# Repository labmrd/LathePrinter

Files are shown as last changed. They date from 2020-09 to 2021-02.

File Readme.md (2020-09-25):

# Lathe 3D Printer

This documentation package includes all of the instructions, materials, models, and code required to construct your own version of the University of Minnesota Medical Robotics and Devices Lab Lathe 3D printer developed by John Huss. This open source design allows a user to create 3D printed balloon catheter segments, for use in constructing robots or other cylindrical 3D printed objects.

## Links to the lab:
- [Research lab](http://dept.me.umn.edu/labs/mrd/)
- [Project motivation](http://dept.me.umn.edu/labs/mrd/Soft_Robots.shtml)

Included in this design are the files needed to recreate the complete fused filament fabrication test bench version of this printer plus the preliminary models and instructions for a fiber reinforced photopolymer extrusion version.

## System features:
The printer utilizes a horizontal lathe-style arrangement of axes to print high aspect ratio cylindrical objects more efficiently and accurately than other methods. This is achieved by using a rotating mandrel as a removable deposition surface. This mandrel can be removed after the printing is finished, leaving a hollow, highly accurate cylinder. Additionally, to ensure straightness of the mandrel two counter-rotating motors (one at each end of the long axis) are used to eliminate any torsional strain in the mandrel. The collets at both ends in which the mandrel is held can be moved along the axis to pre-strain the deposition surface to eliminate gravitational sag and any bends in the mandrel.

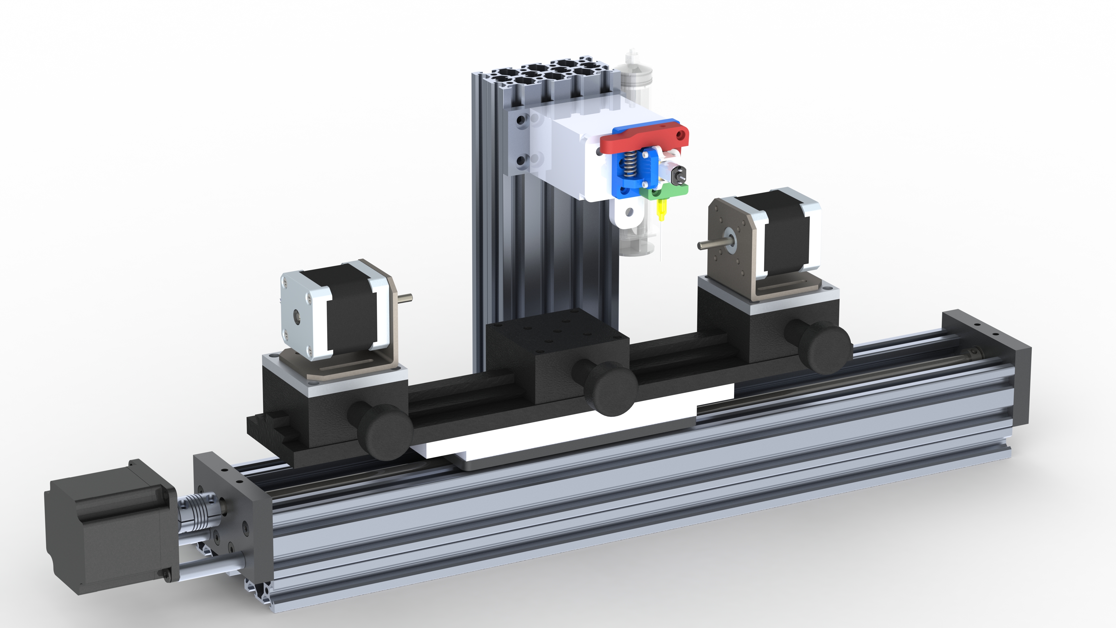
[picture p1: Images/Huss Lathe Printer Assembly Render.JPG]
Solidworks model of the printer


## Coordinates and axis definitions:
This printer operates in a polar coordinate system (R, theta, Z). Z, along the length of the cylinder, is operated by an [OpenBuilds linear actuator](https://openbuildspartstore.com/c-beam-linear-actuator-bundle) and forms the structural base of the printer. The rotational axis, theta (Y axis in the firmware), is operated by two counter-rotating stepper motors mounted to an optics positioning stage on the sliding potion of the Z axis linear carriage. The optics stage allows for fine tuning of the distance between the two theta axis motors to accommodate different length mandrels. Additionally, a third optics stage between motor mounts provides a convenient location to mount any measuring equipment or dial indicators. The final axis, R (X in firmware), is vertical and is currently entirely manual. Motion of the R axis is achieved by adjusting the head mount linear stage attaching the nozzle to the head support column. One final minor adjustment axis is available to move the print head forwards and backwards for calibration by adjusting the second dial on the head mount linear stage. This minor axis allows the user to position the head precisely over the mandrel.

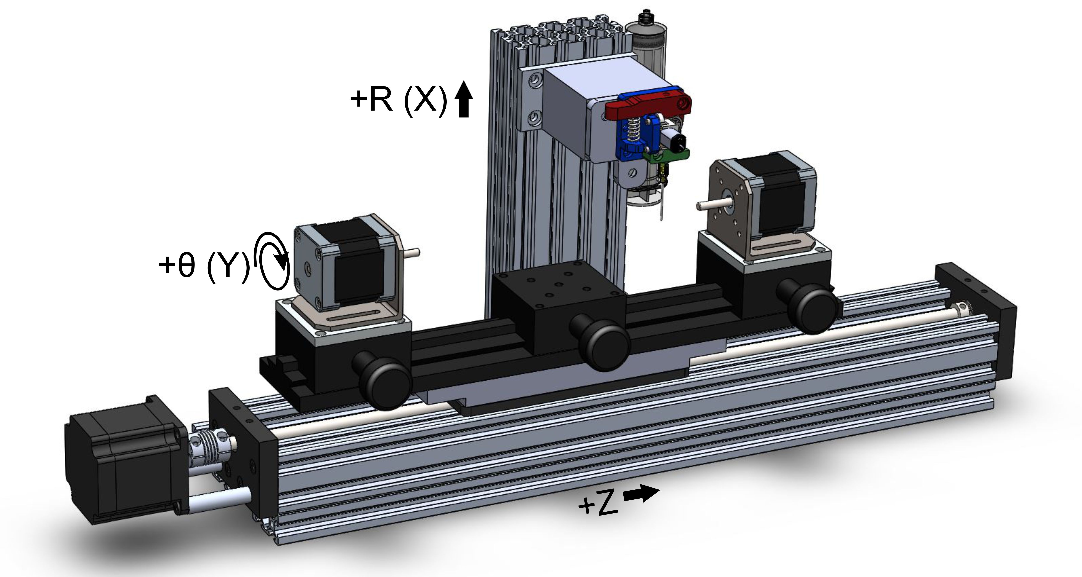
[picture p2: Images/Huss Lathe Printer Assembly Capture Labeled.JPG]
Axes


## Software and slicing:
This printer accepts standard 3D printer G-code, but with some restrictions. The system will fail to print if the requested nozzle position is within R=1mm (representing the minimum R position because of the mandrel). Traditional slicers prepare 3D printer G-code by turning the CAD model into a series of 2D layers from -Z to +Z, which is not how this printer is constructed. This system requires G-code with layers ordered from -R to +R. If the user only needs single layer thickness models, they should use a commonly available feature of slicers often called "vase mode" to create single nozzle width walls. In this case, the walls are layers. To achieve thicker cylinders there are a few options. 
1. Run the print again with the manual R axis set slightly higher and adjust the extrusion rate modifier accordingly in the control console. 
2. If the user automates the R axis, slice a second cylinder model with a slightly wider radius and print that onto the first model. 
3. Generate or modify G-code using a different method such as a custom MATLAB or Python script, or process existing G-code files into one continuous file.
Slicing models for this printer is the biggest area of needed improvement and will change depending on the user's desired use case. The above methods are suggested starting points for researchers to build from.

## Firmware:
This printer uses a Duet2 Ethernet controller board and an older version of dc42's Duet Firmware package [RepRapFirmware](https://github.com/Duet3D/RepRapFirmware) has been configured for this system. The configuration file and homing files (with comments) are included in this documentation package. The specific G codes supported in this firmware package are [documented here](https://duet3d.dozuki.com/Wiki/Gcode).

## Electronics and Wiring:
The wiring for this project is standard for a 3D printer using stepper motors with a few exceptions. Only one axis requires an end-stop, Z, because R is manual, and theta is continuous. This endstop is not pictured in the CAD files but can be seen mounted to the linear actuator on the left side of the carriage in the photographs. To achieve counter-rotating mandrel motors both motors are plugged into the Z-axis motor ports on the Duet board. Duet supports two Z axis motors in parallel at the hardware level for large print beds. There are two ports connected to the same motor driver chip. To force one motor to spin in reverse of the other, reverse the pin-out of one pair of wires on the stepper motor. This will cause it to rotate the other way compared to the first motor. It does not matter which pair you swap as long as they are from the same winding. You can check for continuity between each pair of wires to know which go together before swapping. The Z axis motor ports on the board are configured in firmware to act as the rotational axis of the polar printer instead of as the Z axis.

### Wiring diagram:
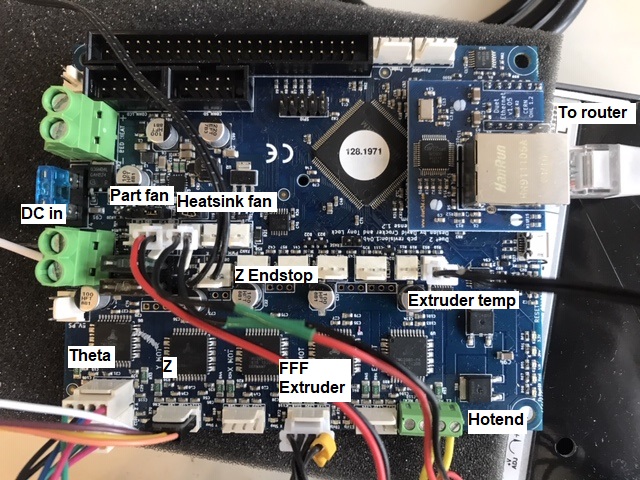
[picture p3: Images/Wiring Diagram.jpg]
Electronics wiring diagram


### Dual theta stepper motor wire swap
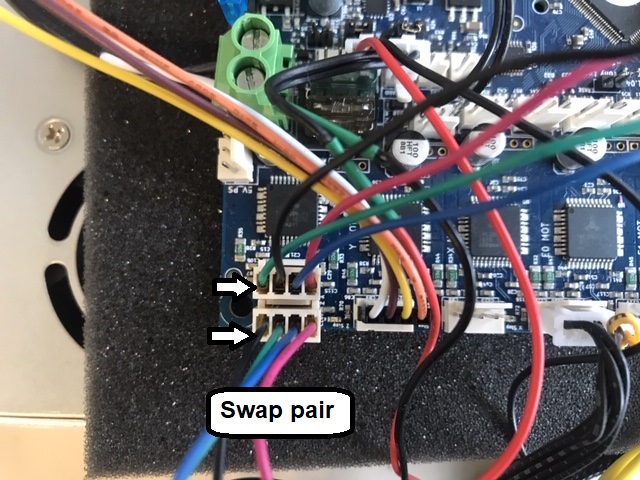
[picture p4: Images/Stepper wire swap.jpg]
Stepper motor wire swap


## Hardware design:
Many components of this printer are available for purchase or can be made using other common 3D printers and machining techniques. The main structure of this system is created from aluminum extrusions, assembled using T-slot nuts, bolts, and brackets. The full Bill of Materials in included for a more detailed view of all necessary components. Most of the mounting hardware is not shown in the CAD files, so use the pictures to see how I assembled it. Feel free to make changes. See the Images folder for detailed photos of the assembly.

## Extrusion systems:
Two extrusion systems currently exist for this printer, a traditional fused filament fabrication extruder, and an experimental fiber reinforced photopolymer co-extruder. The FFF extruder is a standard Creality CR-10 extruder and hotend assembly adapted to fit onto the head column. The experimental co-extrusion fiber/photopolymer system is based on a CR-10 extruder, but highly modified with experimental 3D printed components. Once complete this second system will allow a user to create highly elastic air-tight cylinders with built-in strain-limiting fibers. These fibers can be used to modify the behavior of the cylinders when they are inflated, which is an ongoing research topic within the MRD Lab.

## Example FFF print:
A sample part is included along with instructions in video form on how to get started, from printer assembly to firmware installation, slicing and printing. This sample part is a simple one-layer thick cylindrical model.

### Getting connected if your network uses DHCP
In a university research lab setting I found it difficult to configure the printer to always use a static IP address. There are three main options, with some clearly better than others. The first and best option is to let your network manager assign this device a static IP using the MAC address listed in the config.g file (you can change this if there is a conflict). If that isn't an option you can set up your own small offline network and configure your router to assign the printer a static IP. This is how the printer is currently configured. Alternatively, you can connect directly to a computer but I found it simpler to use a router. Finally, and not recommended, you can let the printer use DHCP on the university network and interrogate the printer over USB to discover its assigned IP address. To do this connect via the USB cable and use a slicing program (I used Matter Control) that has a Terminal window. Connect using the terminal and send M552 to find out the current network settings.

### Notes on choosing your own hardware and electronics:
Many of the components for this printer were chosen primarily due to their availability in the lab already and my familiarity with them. If you want to choose different components (possibly cheaper) that is certainly an option. The full capabilities of the power supply, mainboard, and even the full accuracy of the optics components are not being used in this current form, but for a research platform it is helpful to eliminate any potential issues from incompatible or underperforming equipment. It may be possible to extract the motors, power supply, and electronics from a more inexpensive 3D printer to build this system, but I haven't tested compatibility with anything else. Possible hurdles may arise with the polar setup if a different mainboard/firmware combination doesn't support this kinematics type.

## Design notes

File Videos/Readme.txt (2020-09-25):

Unfortunately, a few of these videos are missing some content. Two of the videos were recorded Zoom meetings with a secondary camera pointed at the phyical printer. This wasn't captured properly in the recordings. Use your imagination I guess.

Videos are hosted in Google Drive, here:
https://drive.google.com/drive/folders/1oRndGqx4MNpRWvz8KzQ8WXYX7neBrAih?usp=sharing

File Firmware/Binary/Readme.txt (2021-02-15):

This is the binary to install through Duet Web Control onto your Duet board. This is the version I used, which is likely now outdated. Update as you see fit. 
As of 2/15/2021 it looks like the firmware project is located at https://github.com/Duet3D/RepRapFirmware

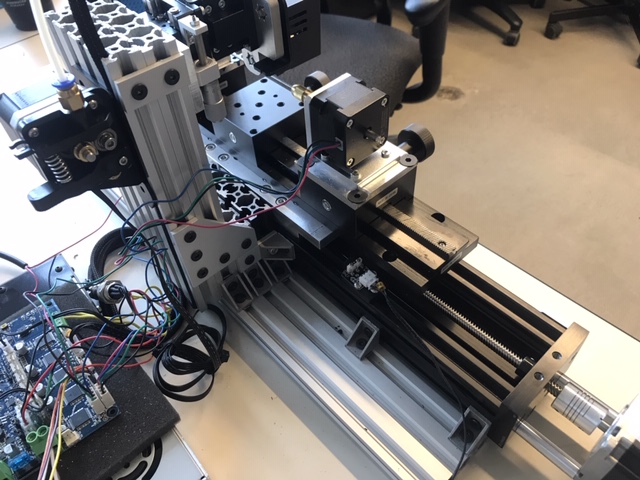
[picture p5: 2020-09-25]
Images/Left 2.jpg

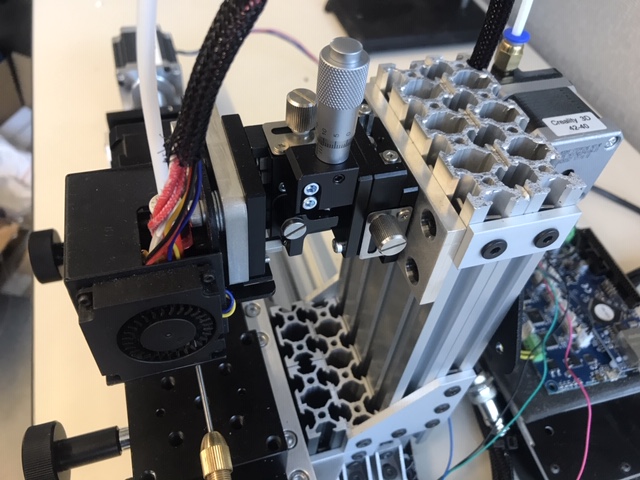
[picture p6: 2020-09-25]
Images/Right Top.jpg

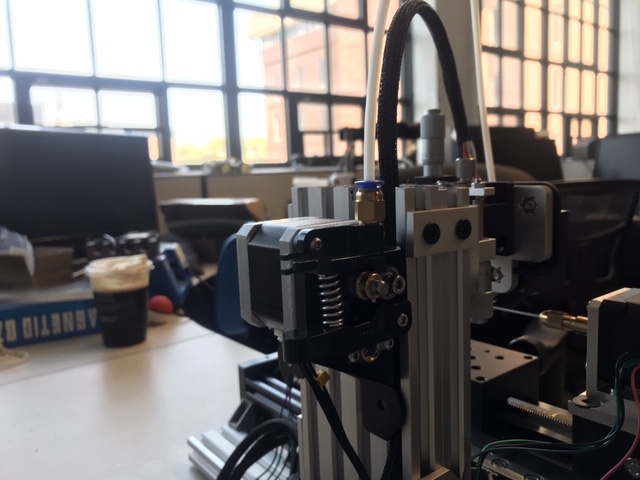
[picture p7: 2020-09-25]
Images/Extruder.jpg

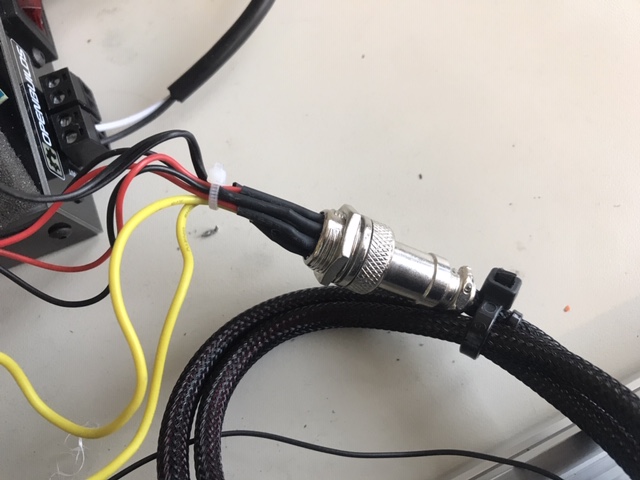
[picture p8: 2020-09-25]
Images/CR10 Wire Bundle.jpg

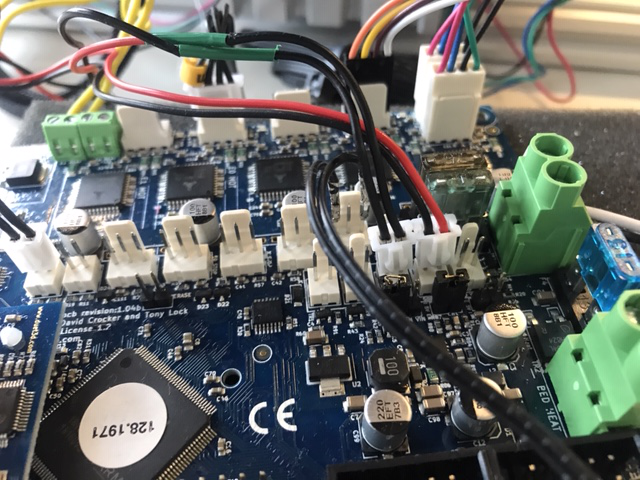
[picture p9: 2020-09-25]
Images/Board Back.jpg

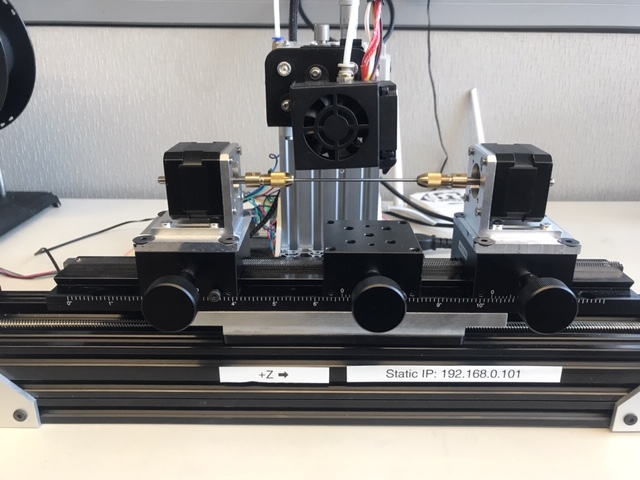
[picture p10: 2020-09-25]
Images/Front.jpg

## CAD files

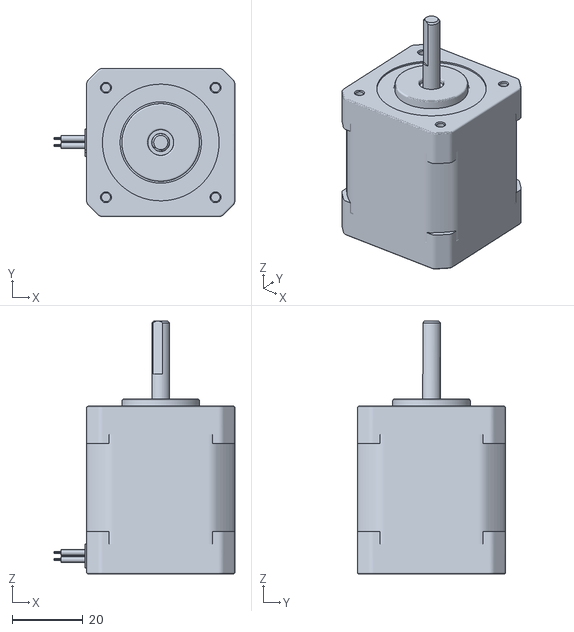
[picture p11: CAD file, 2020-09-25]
CAD/STL Assembly/LathePrinter - Z Carriage Assembly-1 NEMA17 Stepper-2.STL
51.2 x 42.0 x 71.6

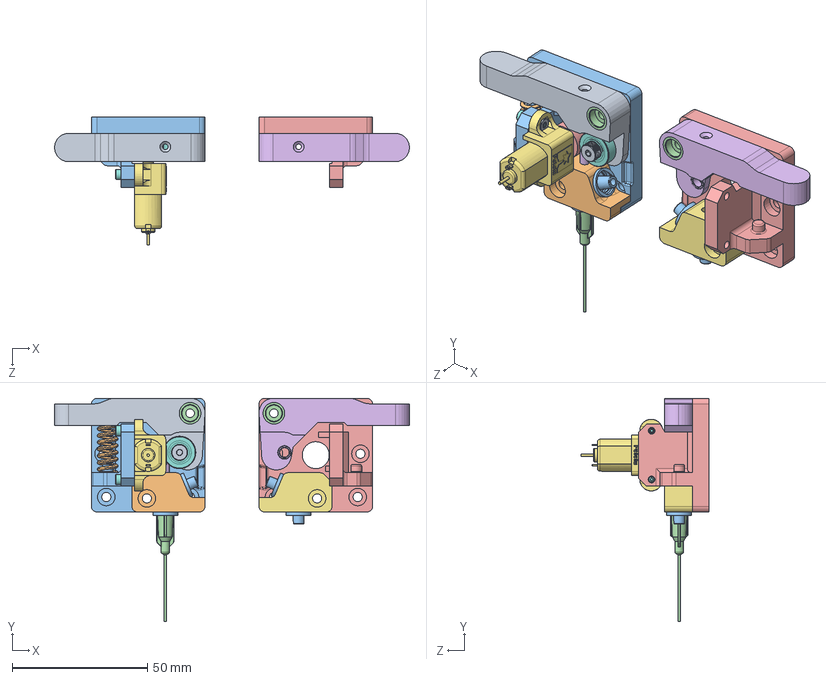
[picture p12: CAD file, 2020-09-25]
CAD/Solidworks 2019 Assembly/Experimental Extruder Dual Extruder.SLDASM
131.3 x 82.6 x 47.3 mm
ExtruderCR10 lever mirrored
ExtruderCR10 spring
Extruder custom base mirrored
ExtruderCR10 bushing x 2
SLA Printed Driver
52335K910 TUBING MADE WITH PTFE cut to size
micro-metal-gearmotor-extended-with-1086-bracket (1)
91290A015_BLACK-OXIDE CLASS 12.9 SOCKET HEAD CAP SCREW x 2
91828A111_TYPE 18-8 STAINLESS STEEL HEX NUT
SLA Printed Manifold
Luer male print with manifold x 4
Syringe Needle, With Luer
MirrorExtruder custom base
MirrorExtruderCR10 lever
MirrorPart21
7804K102_STAINLESS STEEL BALL BEARING
91273A351_SAME-SIZE THREAD 18-8 SS SHOULDER SCREW

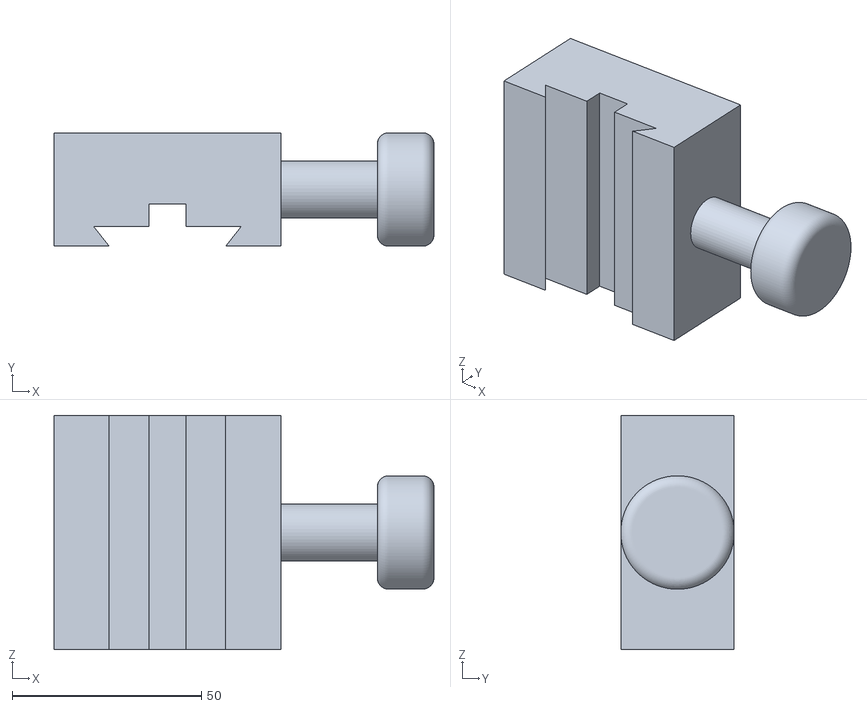
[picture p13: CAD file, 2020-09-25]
CAD/STL Assembly/LathePrinter - Z Carriage Assembly-1 Edmund Optics Knob Stage-5.STL
100.5 x 30.0 x 62.0

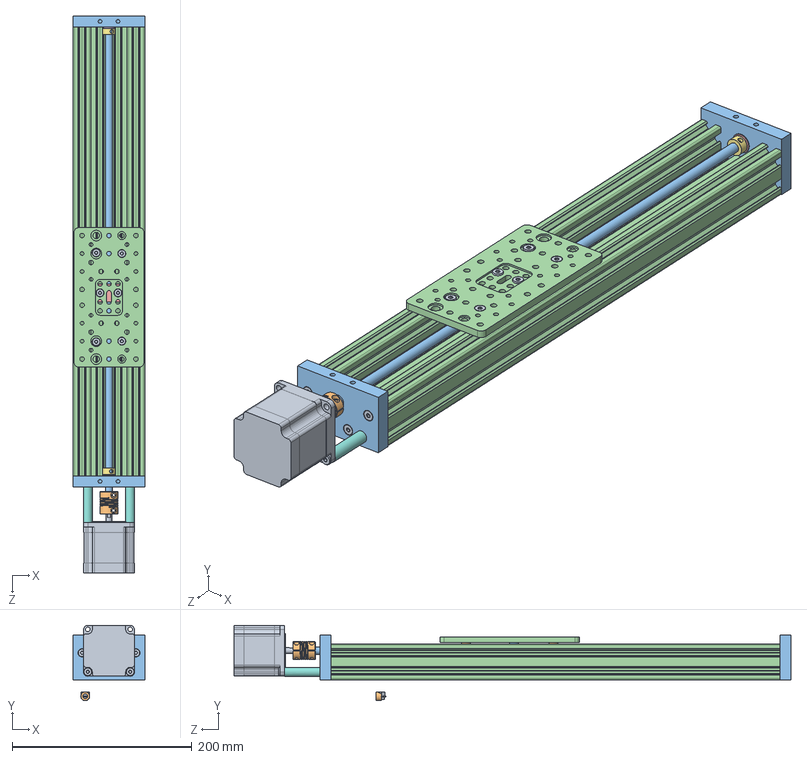
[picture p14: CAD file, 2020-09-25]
CAD/Solidworks 2019 Assembly/C-Beam Doublewide Linear Actuator 500mm.SLDASM
80.0 x 84.0 x 620.0 mm
Low Profile Screw M5 x 16
Nylon Insert Lock Nut M5 x 6
C-Beam End Mount x 2
C-Beam 40x80x500 Linear Rail
Ball Bearing 8 x 16 x 5 x 2
Shim Washer 8mm x 2
Lock Collar 8mm x 2
Aluminum Spacer 40mm x 2
Nema 23 Stepper Motor
Flexible Coupling 0.25in x 8mm
8mm leadscrew 540mm
Double CB-Gantry Plate
8mm Acme Nut Block
Xtreme Mini V Wheel x 4
Ball Bearing 5 x 10 x 4.2 x 8
Precision Shim 8 x 5 x 1 x 8
Mini Eccentric Spacer 6mm x 4
Aluminum Spacer 6mm x 4
Aluminum Spacer 3mm x 2

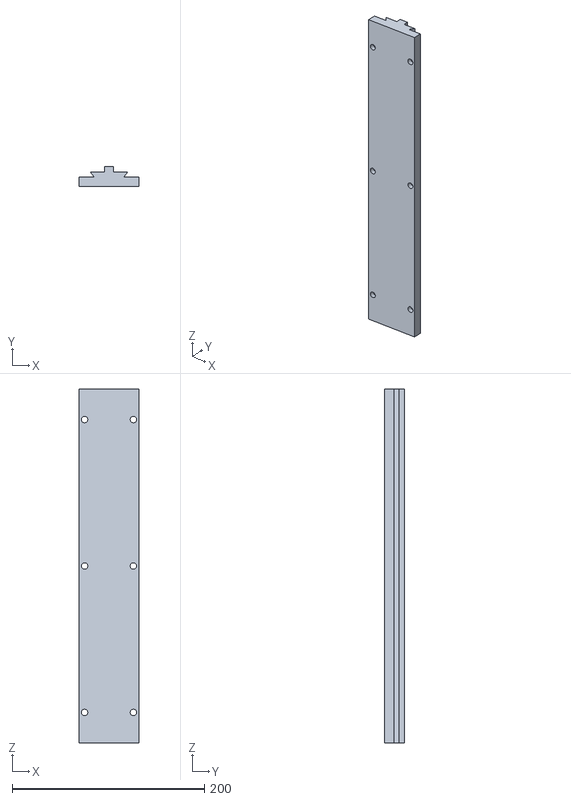
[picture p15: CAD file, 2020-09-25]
CAD/STL Assembly/LathePrinter - Z Carriage Assembly-1 Edmund Optics Linear Bearing-1.STL
62.0 x 21.1 x 368.5

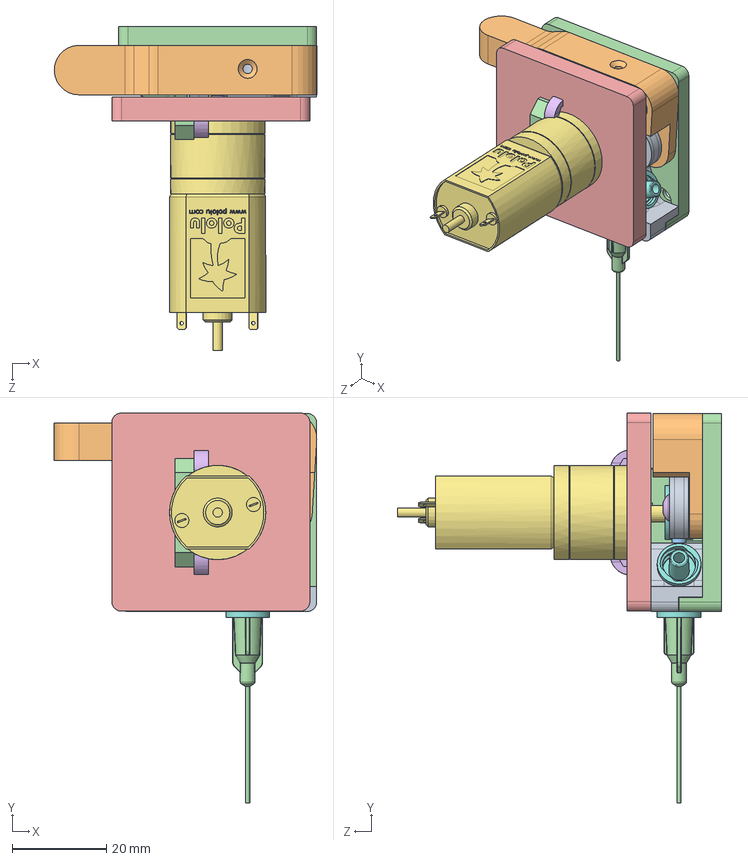
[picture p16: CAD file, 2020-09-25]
CAD/Solidworks 2019 Assembly/Extruder mini gear motor custom metal liner.SLDASM
55.7 x 82.7 x 68.7 mm
ExtruderCR10 idler
ExtruderCR10 lever
ExtruderCR10 spring
Extruder custom base
ExtruderCR10 bushing
ExtruderCR10 M3
94510A240_BRASS SCREW-TO-EXPAND INSERTS
52335K910_METRIC EXTREME-TEMP TUBING MADE WITH PTFE
micro-metal-gearmotor-extended-with-1086-bracket (1)
Syringe Needle, Without Luer
Luer male x 2

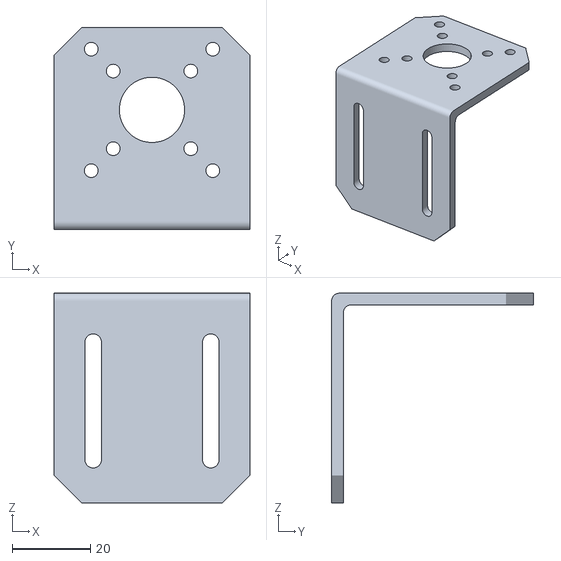
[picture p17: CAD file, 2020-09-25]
CAD/STL Assembly/LathePrinter - Z Carriage Assembly-1 Mandrel Motor Bracket-2.STL
50.0 x 51.5 x 53.5

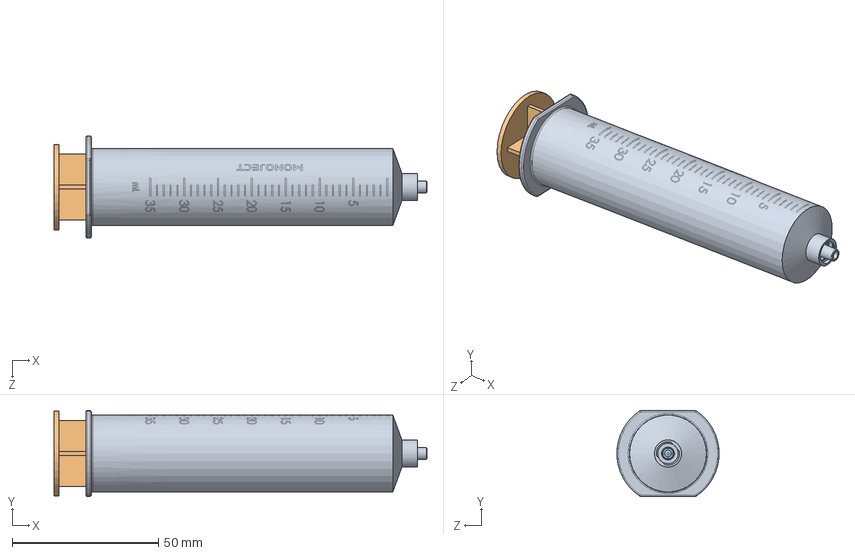
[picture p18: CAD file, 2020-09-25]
CAD/Solidworks 2019 Assembly/014-0244 35cc Syringe.SLDASM
127.4 x 29.4 x 34.9 mm
014-0244 ITEM1 Barrel
014-0244 ITEM2 Plunger
014-0244 ITEM3 Gasket

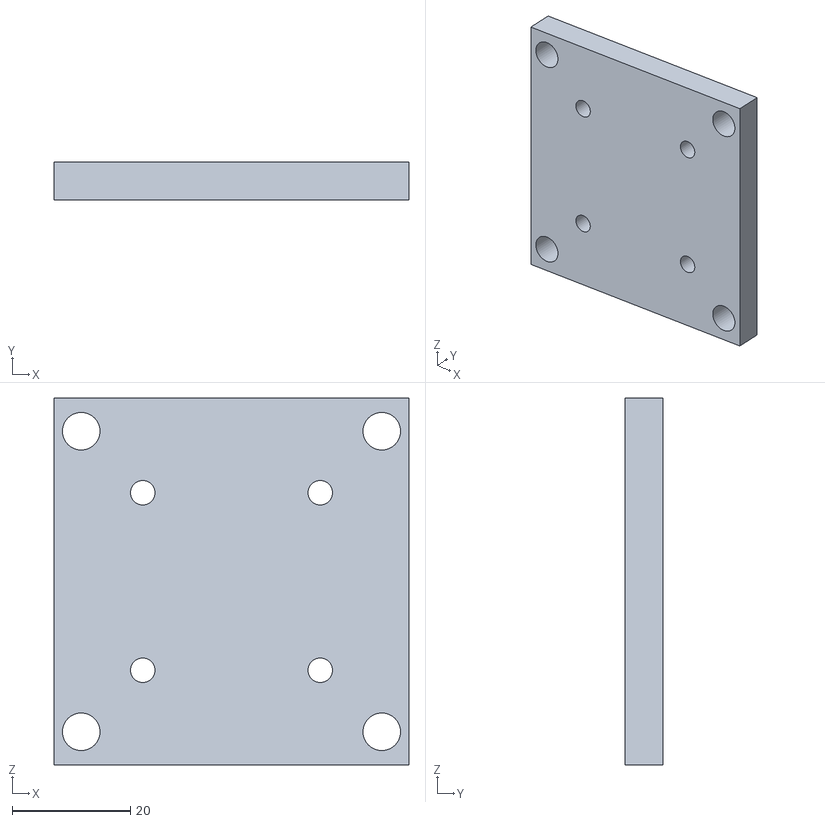
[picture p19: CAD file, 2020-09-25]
CAD/STL Assembly/LathePrinter - Z Carriage Assembly-1 Mandrel Motor Plate-1.STL
60.0 x 6.35 x 62.0

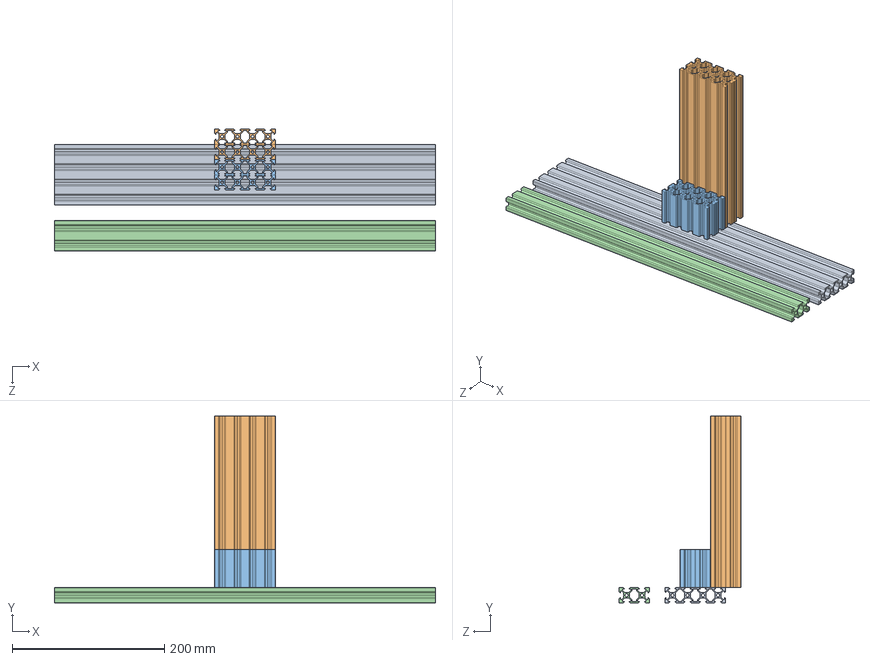
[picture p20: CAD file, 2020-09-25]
CAD/Solidworks 2019 Assembly/Aluminum Extrusion Frame.SLDASM
500.0 x 245.0 x 160.0 mm
V-Slot 20x80x500 Linear Rail
V-Slot 20x80x225 Linear Rail x 2
V-Slot 20x80x50 Linear Rail x 2
V-Slot 20x40x500 Linear Rail

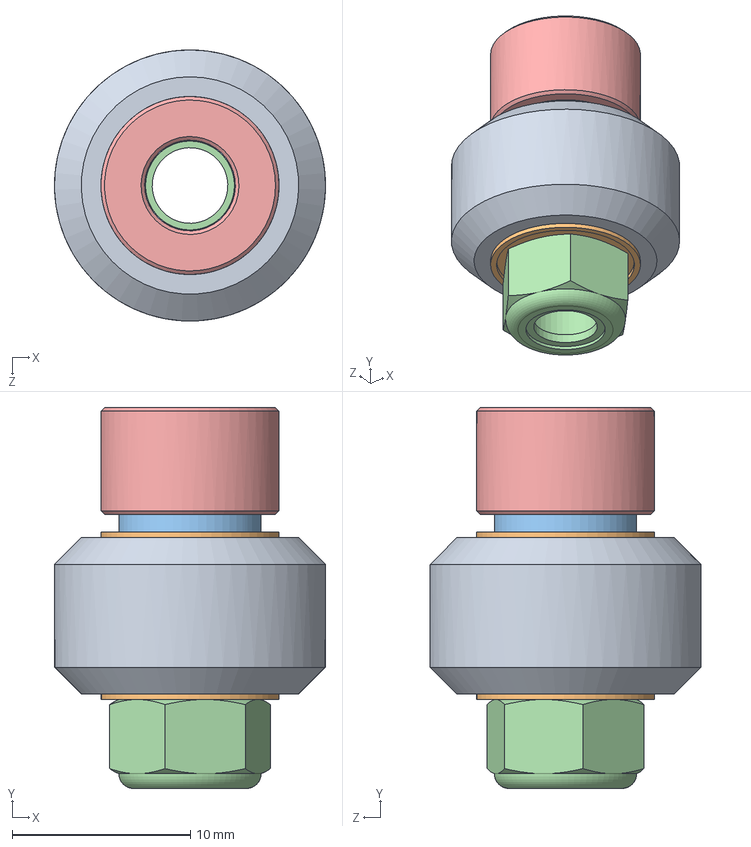
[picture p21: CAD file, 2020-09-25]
CAD/Solidworks 2019 Assembly/Xtreme Mini V Wheel.SLDASM
15.2 x 21.4 x 15.2 mm
Xtreme Mini V Wheel
Ball Bearing 5 x 10 x 4.2 x 2
Precision Shim 8 x 5 x 1 x 2
Nylon Insert Lock Nut M5
Aluminum Spacer 6mm

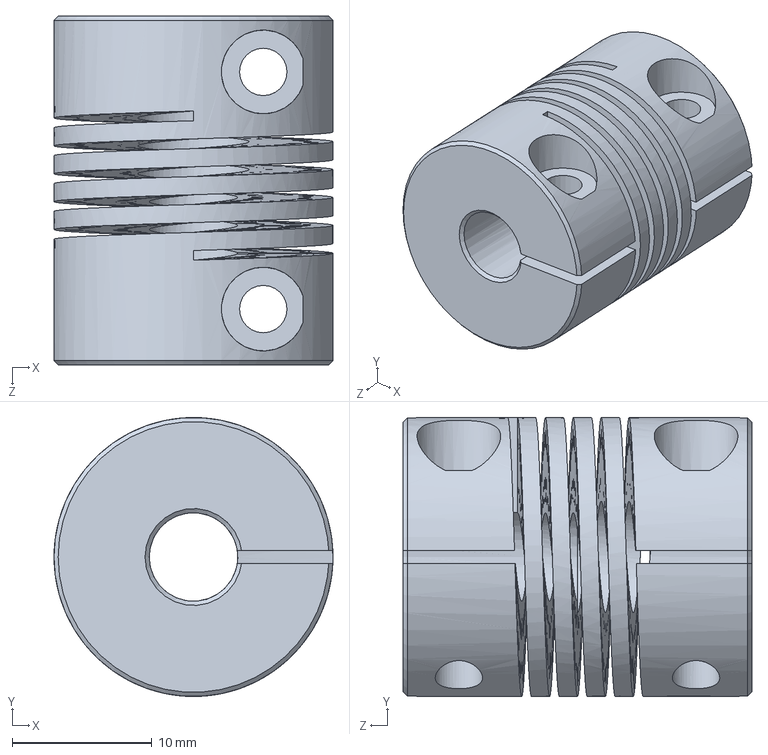
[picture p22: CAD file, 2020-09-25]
CAD/Solidworks 2019 Assembly/Flexible Coupling 0.25in x 8mm.SLDPRT
20.0 x 20.0 x 25.0 mm

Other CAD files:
CAD/Solidworks 2019 Assembly/Z Carriage Assembly.SLDASM
CAD/STL Assembly/LathePrinter - Z Carriage Assembly-1 Edmund Optics Knob Stage-4.STL
CAD/STL Assembly/LathePrinter - Z Carriage Assembly-1 Mandrel Motor Bracket-1.STL
CAD/STL Assembly/LathePrinter - Z Carriage Assembly-1 Mandrel Motor Plate-2.STL
CAD/STL Assembly/LathePrinter - Z Carriage Assembly-1 Edmund Optics Knob Stage-1.STL
CAD/STL Assembly/LathePrinter - Z Carriage Assembly-1 NEMA17 Stepper-1.STL
CAD/STL Assembly/LathePrinter - 014-0244 35cc Syringe-1 014-0244 ITEM1 Barrel-1.STL
CAD/STL Assembly/LathePrinter - 014-0244 35cc Syringe-1 014-0244 ITEM2 Plunger-1.STL
CAD/STL Assembly/LathePrinter - 014-0244 35cc Syringe-1 014-0244 ITEM3 Gasket-1.STL
CAD/STL Assembly/LathePrinter - 94855A247_LOW-STRENGTH STEEL SQUARE NUT-1.STL
CAD/STL Assembly/LathePrinter - Aluminum Extrusion Frame-1 V-Slot 20x40x500 Linear Rail-1.STL
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
